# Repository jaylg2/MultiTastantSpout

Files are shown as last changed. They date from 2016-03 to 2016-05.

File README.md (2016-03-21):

# MultiTastantSpout
This directory contains open source design materials for a rodent behavioral environment for learning from positive and negative events. These materials are for an Arduino controlled lick spout that controls delivery of small amounts of three different tastants, playing of 2 different tones (11KHz and 4KHz in this design), and timing of an in-cage light cue. 

See MultiTast_Overview for information on the build

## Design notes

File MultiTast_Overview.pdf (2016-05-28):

MultiTastant Spout
Construction Instructions
Nathan V-C, Ph.D.
3/9/2016

Overview:
This directory contains open source design materials for a rodent behavioral environment for learning from positive and negative events. These materials are for an Arduino controlled lick spout that controls delivery of small amounts of three different tastants, playing of 2 different audio cue tones (11KHz and 4KHz in this design), and timing of an in-cage light cue.

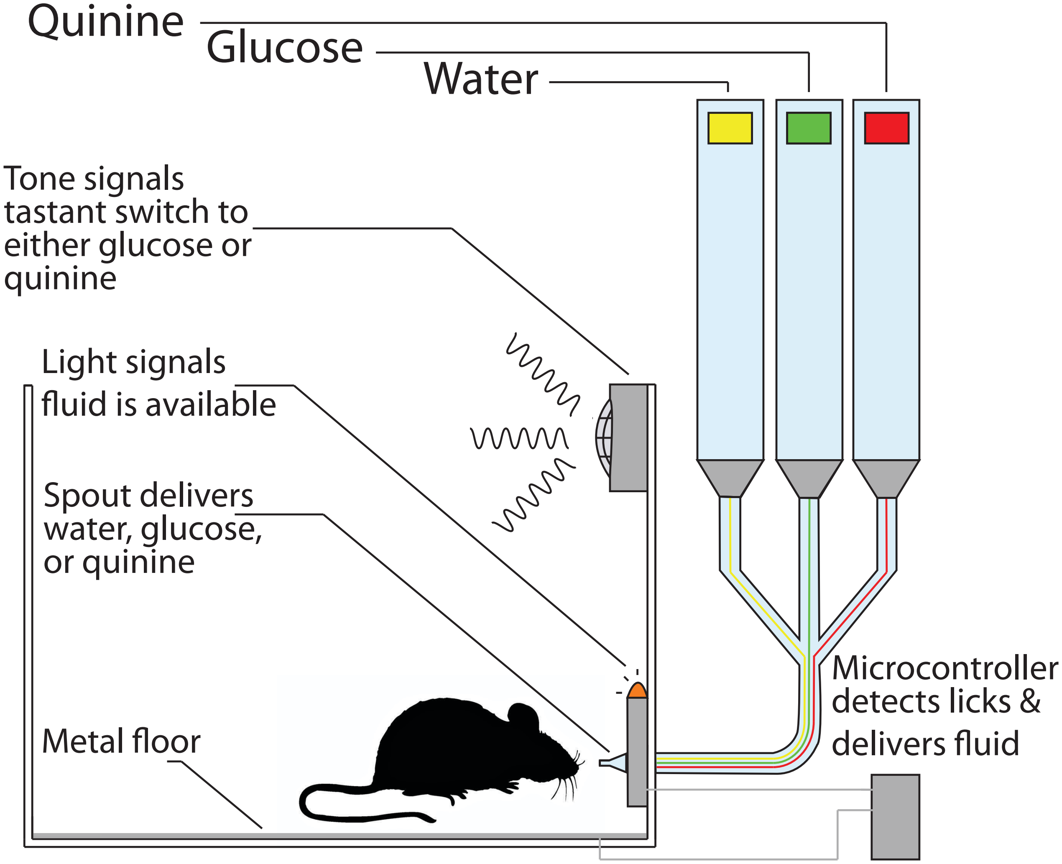
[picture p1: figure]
Quinine Glucose Water; Tone signals tastant switch to either glucose or quinine; Light signals fluid is available; Spout delivers water, glucose, or quinine; Metal floor; Microcontroller detects licks & delivers fluid

Overall the system contains three components:

### 1. Spout Control Board (Arduino Uno Shield)

Eagle and Gerber design files contained in: 3tastsp_v7_resistorcooldrive_battcheck/
This is an Arduino shield contains hardware to control solenoid valves that deliver tastants, LED lights that inform the experimentalist about task events, a calibration button, location for analog-input signal that cues trial type, location for the raw analog input lick signal (through BNC connectors), and an HDMI plug that transmits 8 digital output data signals to your preferred data acquisition system. This control board is placed outside of the behavioral environment (typically a closed sound attenuated cupboard or box). This circuit board design can be sent out to a fabrication company. I use Seeedstudio and these gerber files match their production requirements.

### 2. Spout Interface Board

Eagle and Gerber design files contained in: sptinterface_v4_battcheck/

This printed circuit board delivers cues and power to the solenoid valves that control tastant delivery, the internal cage cue light, some circuitry to protect the lick signal voltage from noise and current draw elsewhere in the system, and produces two cue tones using 555 timer circuits. This board needs to be placed near the spout assembly (typically inside the behavioral enclosure, near but not inside the cage). This design has a feature that if you wish to switch to IR lick detection, there is a plug and circuitry available for that. With this design you must choose between a raw voltage signal lick detection (where the mouse is on a grounded metal cage floor) and IR lick detection. The current spout design does not support IR detection but this is do-able, and this board is set up both to run 5V power to an IR emitter, and to detect analog output from an IR detector. Also, the lick detection circuit is consolidated to the left of the board, with separation possible from the right part of the board that generates tones and controls valves. I designed this board this way so the same system can be adapted to a system where valves need to be separate from the spout (for example, when combined with electrophysiological recording). This PCB can be sent out to a fabrication company. I use Seeedstudio and these gerber files match their production requirements.

### 3. Spout Assembly

OpenSCAD and .stl design files contained in: spoutassembly/
The spout itself is hand built from thin steel 24 gauge tubing arranged in a cylinder and that then interfaces with barbed connectors to link to solenoid valves that deliver the tastant. This spout assembly also holds the solenoid valves. 3 wires from the spout connect to the Spout Interface Board, the LED power, Ground, and a wire connected to the metal spout. I’ve included an OpenSCAD and .stl file of the parts needed for the spout assembly here

These three components are included in these design files. In addition to these three components, you will need a source to generate an analog input signal that cues trial type (I use a NIDAQ card), and Arduino UNO (loaded Arduino script PCB_3tast_v29_3tnblank_public_switchpins.ino or your own modification), a cage and behavioral enclosure, a set of computer speakers to play the tones, and a 9V battery to power the tone production.

At this time, an initial nearly complete parts list is available in this directory (excel file). Construction instructions are still being compiled, but if you would like to build a rig like this and need more complete information before I have updated, please don’t hesitate to contact me via github.

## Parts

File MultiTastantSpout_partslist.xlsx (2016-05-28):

Multitastant spout parts list and cost calculator (Not including data acquisiton or computer) |  |  |  |  |  | Total Cost/rig: | $447.11
Enter number of each component you are ordering parts for: |  | 5 | 5 | 5 |  | Cost/order: | $2235.56
Calculate Cost per single version of each component: |  | $120.74 | $15.28 | $311.09
Type of Part | Link | Control | Spt Interface | Spout | Cost/each | Cost/setup | Cost/Control | Cost/Interface | Cost/Spout
Arduino Uno microcontroller | https://www.sparkfun.com/products/11021 | 1 | 0 | 0 | $24.95 | $24.95 | $24.95 | $0.00 | $0.00
Set of four colored LEDs (one each: red/green/yellow/blue) | https://www.sparkfun.com/products/12062 | 1 | 0 | 0 | $0.59 | $0.59 | $0.59 | $0.00 | $0.00
Tactile button (sparkfun) | https://www.sparkfun.com/products/9190 | 1 | 0 | 0 | $0.50 | $0.50 | $0.50 | $0.00 | $0.00
9-pin female connectors (digikey) | http://www.digikey.com/product-detail/en/PPPC091LFBN-RC/S7042-ND/810181 | 4 | 0 | 0 | $0.69 | $2.76 | $2.76 | $0.00 | $0.00
HDMI connector | http://www.digikey.com/product-search/en?pv7=2&k=609-4614-1-ND&mnonly=0&newproducts=0&ColumnSort=0&page=1&quantity=0&ptm=0&fid=0&pageSize=25 | 1 | 0 | 0 | $0.69 | $0.69 | $0.69 | $0.00 | $0.00
BNC male connectors | http://www.mouser.com/ProductDetail/TE-Connectivity-AMP/1-1337543-0/?qs=sGAEpiMZZMvlX3nhDDO4AKImBYvddvkFKOqsKyyMJX4= | 2 | 2 | 0 | $1.15 | $4.60 | $2.30 | $2.30 | $0.00
Male 4-wall 16 pin ribbon connector port (3M) | http://www.mouser.com/ProductDetail/3M-Electronic-Solutions-Division/30316-6002HB/?qs=sGAEpiMZZMujYETmGQpRztX3nUeKjWBk | 1 | 1 | 0 | $0.77 | $1.54 | $0.77 | $0.77 | $0.00
Shield pins to connect to Arduino (31 pins total needed, order strip of 40): | http://www.digikey.com/product-detail/en/4-103741-0/A26509-40-ND/297917 | 1 | 0 | 0 | $1.82 | $1.82 | $1.82 | $0.00 | $0.00
330 Ohm resistors | http://www.digikey.com/product-detail/en/stackpole-electronics-inc/CF14JT330R/CF14JT330RCT-ND/1830338 | 4 | 2 | 0 | $0.04 | $0.24 | $0.16 | $0.08 | $0.00
10K resistors | http://www.digikey.com/product-detail/en/stackpole-electronics-inc/CF14JT10K0/CF14JT10K0CT-ND/1830374 | 1 | 1 | 0 | $0.04 | $0.08 | $0.04 | $0.04 | $0.00
1K resistors | http://www.digikey.com/product-detail/en/stackpole-electronics-inc/CF14JT1K00/CF14JT1K00CT-ND/1830350 | 4 | 4 | 0 | $0.04 | $0.32 | $0.16 | $0.16 | $0.00
8 Pin DIP sockets | http://www.digikey.com/product-detail/en/DILB8P-223TLF/609-4717-ND/4292069 | 0 | 3 | 0 | $0.17 | $0.52 | $0.00 | $0.52 | $0.00
TIP122 NPN Transistors | http://www.digikey.com/product-detail/en/TIP122/TIP122FS-ND/458797 | 0 | 3 | 0 | $0.54 | $1.62 | $0.00 | $1.62 | $0.00
555 timers | http://www.digikey.com/product-search/en?x=0&y=0&lang=en&site=us&keywords=LM555CNNS | 0 | 2 | 0 | $0.93 | $1.87 | $0.00 | $1.87 | $0.00
9 Volt battery holder | http://www.digikey.com/product-detail/en/BH9VPC/BH9V-PC-ND/31510 | 0 | 1 | 0 | $1.60 | $1.60 | $0.00 | $1.60 | $0.00
3-pin shrouded male connector | http://www.digikey.com/product-detail/en/5-103735-2/A33924-ND/1122487 | 0 | 3 | 0 | $1.05 | $3.15 | $0.00 | $3.15 | $0.00
4-pin shrouded male connector for IR option | http://www.digikey.com/product-detail/en/te-connectivity-amp-connectors/5-103735-3/A33926-ND/1122489 | 0 | 1 | 0 | $1.66 | $1.66 | $0.00 | $1.66 | $0.00
Crimp connectors | http://www.digikey.com/product-detail/en/1-104479-3/A34249-ND/11258912 | 0 | 0 | 12 | $0.23 | $2.71 | $0.00 | $0.00 | $2.71
1-pin shrouded connector socket | http://www.digikey.com/product-detail/en/te-connectivity-amp-connectors/1-1123824-1/A30708-ND/686939 | 0 | 0 | 2 | $0.19 | $0.38 | $0.00 | $0.00 | $0.38
1-pin plug for shielding | http://www.digikey.com/product-detail/en/te-connectivity-amp-connectors/1-1123823-1/A30525-ND/686690 | 0 | 0 | 1 | $0.10 | $0.10 | $0.00 | $0.00 | $0.10
1-pin connector crimp connections | http://www.digikey.com/product-detail/en/te-connectivity-amp-connectors/1123721-2/A100446CT-ND/2233212 | 0 | 0 | 1 | $0.17 | $0.17 | $0.00 | $0.00 | $0.17
2-pin shrouded male connectors for valves | http://www.digikey.com/product-detail/en/5-103735-1/A33921-ND/1122484 | 0 | 0 | 4 | $0.70 | $2.80 | $0.00 | $0.00 | $2.80
LM258N op-amp | http://www.digikey.com/product-detail/en/LM258N/LM258NFS-ND/1051227 | 0 | 0 | 1 | $0.45 | $0.45 | $0.00 | $0.00 | $0.45
Female 16 pin ribbon connector socket for ribbon cable (3M) | http://www.mouser.com/ProductDetail/3M-Electronic-Solutions-Division/89116-0101/ | 0 | 0 | 2 | $1.05 | $2.10 | $0.00 | $0.00 | $2.10
1.5 Kohms resistor (brown, green, red, gold bands, for ~4KHz tone) | http://www.digikey.com/product-detail/en/stackpole-electronics-inc/CF14JT1K50/CF14JT1K50CT-ND/1830354 | 0 | 1 | 0 | $0.04 | $0.04 | $0.00 | $0.04 | $0.00
270 Kohm resistor (red, purple, yellow, gold, for ~4KHz tone | http://www.digikey.com/product-detail/en/stackpole-electronics-inc/CF14JT270K/CF14JT270KCT-ND/1830409 | 0 | 1 | 0 | $0.04 | $0.04 | $0.00 | $0.04 | $0.00
680 Ohm resistor (blue, gray, brown, gold, for ~11KHz tone) | http://www.digikey.com/product-detail/en/stackpole-electronics-inc/CF14JT680R/CF14JT680RCT-ND/1830346 | 0 | 1 | 0 | $0.04 | $0.04 | $0.00 | $0.04 | $0.00
100 KOhms (brown, black, yellow, gold, for ~11KHz tone) | http://www.digikey.com/product-detail/en/stackpole-electronics-inc/CF14JT100K/CF14JT100KCT-ND/1830399 | 0 | 1 | 0 | $0.04 | $0.04 | $0.00 | $0.04 | $0.00
capacitors for 555 timers (need to check value) | http://www.digikey.com/product-detail/en/FK28C0G1H561J/445-4735-ND/2050084 | 0 | 2 | 0 | $0.23 | $0.47 | $0.00 | $0.47 | $0.00
Voltage regulators | http://www.digikey.com/product-detail/en/LM7805CT/LM7805CT-ND/458698 | 0 | 1 | 0 | $0.62 | $0.62 | $0.00 | $0.62 | $0.00
1A diodes for tone circuit | http://www.digikey.com/product-detail/en/micro-commercial-co/1N4002-TP/1N4002-TPMSCT-ND/773689 | 0 | 2 | 0 | $0.11 | $0.22 | $0.00 | $0.22 | $0.00
3A diodes for valves | http://www.digikey.com/product-detail/en/fairchild-semiconductor/1N5401/1N5401FSCT-ND/1532774 | 0 | 0 | 4 | $0.31 | $1.24 | $0.00 | $0.00 | $1.24
27 KOhm resistor to reduce volume of lower tone (red, purple, orange, gold) | http://www.digikey.com/product-detail/en/stackpole-electronics-inc/CF14JT27K0/CF14JT27K0CT-ND/1830385 | 0 | 1 | 0 | $0.04 | $0.04 | $0.00 | $0.04 | $0.00
2 ¼” bright white LEDs (sparkfun link) | https://www.sparkfun.com/products/9850 | 0 | 0 | 2 | $0.32 | $0.64 | $0.00 | $0.00 | $0.64
1 shrouded 4-pin female connector | http://www.digikey.com/product-detail/en/te-connectivity-amp-connectors/104257-3/A28401-ND/289304 | 0 | 0 | 1 | $0.56 | $0.56 | $0.00 | $0.00 | $0.56
1 shrouded 3 pin female connector | http://www.digikey.com/product-detail/en/104257-2/A28397-ND/289303 | 0 | 0 | 1 | $0.49 | $0.49 | $0.00 | $0.00 | $0.49
BNC T connector (for splitting lick signal to data collection if desired) | http://www.digikey.com/product-detail/en/27-8141/J10096-ND/698063 | 1 | 0 | 0 | $3.00 | $3.00 | $3.00 | $0.00 | $0.00
HDMI cable (for connecting control board to data collection) | http://www.amazon.com/gp/product/B0052SCU8U/ref=ox_sc_act_title_3?ie=UTF8&psc=1&smid=ATVPDKIKX0DER | 1 | 0 | 0 | $3.00 | $3.00 | $3.00 | $0.00 | $0.00
Power cord for Arduino (12V, 1A, less than 1A is not enough power for valves) |  |  |  |  |  | $0.00 | $0.00 | $0.00 | $0.00
Computer speakers | http://www.amazon.com/gp/product/B000R9AAJA/ref=ox_sc_act_title_1?ie=UTF8&psc=1&smid=ATVPDKIKX0DER | 0 | 0 | 1 | $16.49 | $16.49 | $0.00 | $0.00 | $16.49
Four two-pin shrouded female connectors for valves | http://www.digikey.com/product-detail/en/te-connectivity-amp-connectors/104257-1/A28393-ND/289301 | 0 | 0 | 4 | $0.39 | $1.56 | $0.00 | $0.00 | $1.56
Female screwmount BNC connector for speakers | ?? |  |  |  |  | $0.00 | $0.00 | $0.00 | $0.00
NR research “normally closed” solenoid valves, part number | http://nrresearch.com | 0 | 0 | 4 | $62.00 | $248.00 | $0.00 | $0.00 | $248.00
Single valve driver, "Cooldrive ONE Single Valve Driver", model 161D1X250 | http://nrresearch.com | 4 | 0 | 0 | $20.00 | $80.00 | $80.00 | $0.00 | $0.00
2-way luer lock valves | ?? | 0 | 0 | 4 |  | $0.00 | $0.00 | $0.00 | $0.00
3-way luer lock valves | http://bit.ly/1YUbjqb | 0 | 0 | 4 | $8.35 | $33.41 | $0.00 | $0.00 | $33.41
24 gauge steel tubing, approx 30" |  |  |  |  |  | $0.00 | $0.00 | $0.00 | $0.00
1/8” tubing (lots, mcmaster) -- price per foot | http://www.mcmaster.com/#5103k32/=ymy2fa | 0 | 0 | 10 |  | $0.00 | $0.00 | $0.00 | $0.00
1/8” barb connectors (WPI) - I used from this kit, but should be possible to order separately | https://www.wpiinc.com/products/laboratory-supplies/500890-barb-to-tubing-coupler-kit/ | 0 | 0 | 4 |  | $0.00 | $0.00 | $0.00 | $0.00
screw-in Luer Lock connectors for valves (McMaster) | http://www.mcmaster.com/#51525k21/=ymxy71 | 0 | 0 | 8 |  | $0.00 | $0.00 | $0.00 | $0.00
luer lock connection for tubing | http://www.mcmaster.com/#51525k33/=ymxj06 | 0 | 0 | 8 |  |  |  |  | $0.00
Ribbon cable (?? Not sure where to get this, 16 contacts, flat, gray, fits 3M connectors) | ?? |  |  |  |  | $0.00 | $0.00 | $0.00 | $0.00
Other Supplies:
Various BNC cables, 2 long, 1 short, depends on needs of your set-up
18-20 gauge wire in colors as desired for color coding
Foil for shielding speaker wire
Heat shrink tubing
Cage, need to be able to open hole in side for spout, and attach metal tape to floor
10 mL syringes to serve as fluid reservoirs
metal tape for cage floor -- metal tape for duct installation (different than duct tape!) works well
3D printed spout assembly
3D printed syringe reservoir grid and syringe holders
3D printed caps for syringes to keep fluids & valves clean
alligator clip connectors

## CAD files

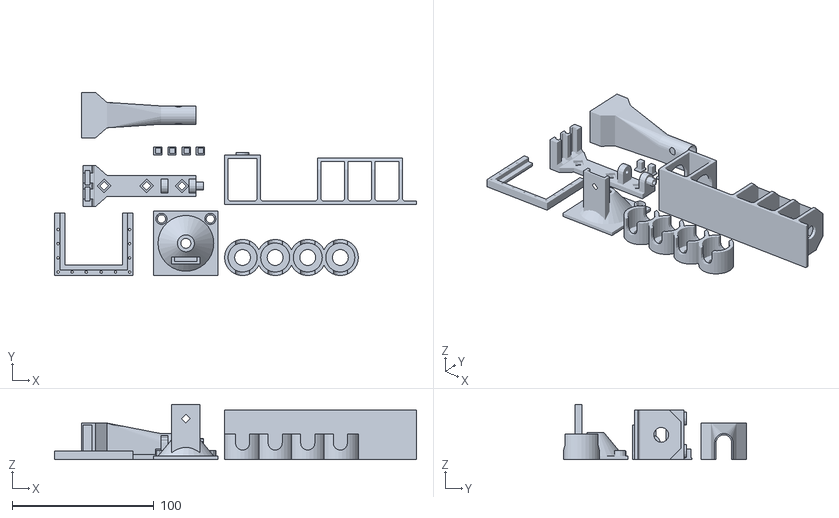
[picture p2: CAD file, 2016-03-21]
spoutassembly/valveandspout_modular_v8_share_allparts.stl
255.5 x 129.2 x 39.0

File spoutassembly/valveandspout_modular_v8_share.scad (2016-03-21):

//------------------
// Generate STL file for multi-tastant spout
//------------------
// Nathan V-C
// 6/2015-10/2015
//------------------

// total height of support from floor of cage
supp_ht=33; 
// total width of support side to side
supp_w=35;
// width at top of support
supp_w_top=10;  // top is actually wider
// length of the spout support portion of the support
supp_ln=60;  
// distance base should extend forward of front edge of spout support
bs_ext=10;

// clearance value -- difference in size for pieces that need to fit in/around each other
cl=1;

// valve dimensions
r_mn=10.25; // radius of solenoid valves
r_big=13; // radius for the large pinch valve
r_tb=5;  // radius of holes for tubes in the valve holder
d_vb=9.2;  // distance to center of tube from flat edge of valve
d_vh=18; // depth of valve holder
th_v=1.5; // thickness for valve holder (for the version with the fluid tray) -- thinner than some other portions (in v6 was the same)

//distance bottom of valves should be from floor of cage -- actually end up thickness higher
v_ht=35; // higher to avoid some tubes running "down" and some running "up" 

thickness=2.5;  // wall thickness throughout assembly
dist_bt=40; // distance between valve support and spout support

// measurements for spout tubing brace attachment
barb_w=10; // width of barb connector
barb_ht=8.4; // height of barb connector
barb_th=3.5; // thickness of barb connector
barb_dpth=1.5;  // depth of groove to hold barb attachments in place
sp_diam=3; // diameter of hole to leave for spout itself (overestimate)

// measurements for nose cone
cn_diam_i=38.5; // inner dimension of nose cone (wall builds around this)
cn_diam_r=6; // inner diameter for opening at back of cone;
cn_depth=19; // depth of cone
led_diam=6; // diameter of hole to leave for LED lights
led_dpth=6.5; // depth of cylinder that LED fits into
led_wall=1;	  // width of wall that holds LED	
led_dist=5.5; // distance of LED hole from edge (dist to center)
br_sq=45.5; // dimension for square part of nose cone
center_ht=45;   // height of center of nose cone from floor, greater than supp_ht
l_cn_br=20; // length of cone brace, distance that flange extends beyond rear of cone to hook onto the tubing brace

// calculations for removing material from spout base
h_sz=(supp_ln-4*thickness)/3;
supp_diag=-0.5*sqrt(2*pow(thickness/2,2));
cube_side=2*min(v_ht,supp_w)/5;
cube_diag=0.5*sqrt(2*pow(cube_side,2));
min_dim=min(v_ht,supp_w);

// dimensions for PCB & battery tray
th_sp=2.5; // thickness of walls in the spout attaching to
th=1.5; // thickness of walls in the pcb tray
pcb_l=90.5; // length of pcb tray
pcb_w=40.5; // width of pcb tray
batt_l=55.5; // dimension for 9V holder
batt_w=31;    // dimensions for 9V holder
batt_th=17;
d_flr=5; // distance of bracket from floor
d_spt=5; // distance of pcb from spout base
gv_dpth=2.5;
batt_o=22.5;
batt_e=8; // amount that holder lip overlaps battery
co=25; // how wide to make cutout for ground wires

//**********
//**********
//------------
// modular part generation -- comment in/out to generate parts that you need
//------------

spout_base(0,0,0);
valve_stand_orig(0,-50,0);
tubing_brace(-(supp_ln+l_cn_br+20),0,0);
spout_shield(-(supp_ln+l_cn_br+20),50,0,1,.5);
nose_cone(-50,-50,0);
cage_bracket(-120,-50,0);

lock_hole_pin(-20,35,0);
lock_hole_pin(-30,35,0);
lock_hole_pin(-40,35,0);
lock_hole_pin(-50,35,0);

// items specific to nathan's set-up
// pcb_tray(0,v_ht+30,0);
// valve_stand_fluidcont(0,-50,0);

//***********
//***********

//---------------------
// Spout base
//----------------------

module spout_base(xp,yp,zp){

translate([xp,yp,zp])

	union(){
		union(){
			difference(){
				union(){
					// spout support
					translate([dist_bt+2*thickness+2*r_mn,0,0])cube([supp_ln,supp_ht,supp_w]);
					//base
					cube([supp_ln+bs_ext+dist_bt+2*thickness+2*r_mn,thickness,supp_w]);
					//valve support
					cube([r_mn*2+2*thickness,v_ht,supp_w]);
					// small circles to help hold valve holder onto support
					translate([thickness+r_mn,v_ht+0.75*thickness,supp_w/2-r_mn-thickness/2])rotate(90,[1,0,0])cylinder(h=thickness, r=r_mn/2-.5,center=false);
					translate([thickness+r_mn,v_ht+0.75*thickness,supp_w/2+r_mn+thickness/2])rotate(90,[1,0,0])cylinder(h=thickness, r=r_mn/2-.5,center=false);
					//extra support for seams
					translate([2*r_mn+2*thickness,supp_diag+thickness/2,0])rotate(45,[0,0,1])cube([thickness,thickness,supp_w]);	
					translate([2*r_mn+2*thickness+dist_bt,supp_diag+thickness/2,0])rotate(45,[0,0,1])cube([thickness,thickness,supp_w]);	
					translate([2*r_mn+2*thickness+dist_bt+supp_ln,supp_diag+thickness/2,0])rotate(45,[0,0,1])cube([thickness,thickness,supp_w]);	
				}
				union(){
					// slant at top of spout support
					translate([-thickness,supp_ht,-0.5*sqrt(2*pow((supp_ht-supp_w_top)/2,2))])rotate(45,[1,0,0])
					translate([dist_bt+2*thickness+2*r_mn,0,0])cube([supp_ln+2*thickness,(supp_ht-supp_w_top)/2,(supp_ht-supp_w_top)/2]);
			
					translate([-thickness,supp_ht,-0.5*sqrt(2*pow((supp_ht-supp_w_top)/2,2))+supp_w])rotate(45,[1,0,0])
					translate([dist_bt+2*thickness+2*r_mn,0,0])cube([supp_ln+2*thickness,(supp_ht-supp_w_top)/2,(supp_ht-supp_w_top)/2]);
			
					// remove squares from spout support to reduce volume
					translate([supp_ln-thickness-h_sz+dist_bt+2*thickness+2*r_mn,thickness,-thickness])cube([h_sz,supp_ht-2*thickness,supp_w+2*thickness]);
					translate([supp_ln-2*thickness-2*h_sz+dist_bt+2*thickness+2*r_mn,thickness,-thickness])cube([h_sz,supp_ht-2*thickness,supp_w+2*thickness]);
					translate([supp_ln-3*thickness-3*h_sz+dist_bt+2*thickness+2*r_mn,thickness,-thickness])cube([h_sz,supp_ht-2*thickness,supp_w+2*thickness]);
			
					// remove square from valve support
					translate([thickness,thickness,-thickness])cube([2*r_mn,v_ht-2*thickness,supp_w+2*thickness]);
			
					// remove material from valve support base in the x direction, use circles to keep printability in z direction
					translate([-thickness,v_ht/2,supp_w/2])rotate(90,[0,1,0])cylinder(h=4*thickness+2*r_mn, r=min_dim/2-2*thickness);
			
					// remove material from spout support base in the x direction, use circle to keep printability in z direction
					translate([dist_bt+thickness+2*r_mn,supp_ht/2+2.5,supp_w/2])rotate(90,[0,1,0])cylinder(h=2*thickness+supp_ln, r=(supp_ht-supp_w_top-thickness)/2-2*thickness);
			
					// remove locking holes
					union(){
						translate([0.25*supp_ln+dist_bt+2*thickness+2*r_mn,supp_ht-thickness,supp_w/2])rotate(-90,[1,0,0])lock_hole_btm(0,0,0);
						translate([0.75*supp_ln+dist_bt+2*thickness+2*r_mn,supp_ht-thickness,supp_w/2])rotate(-90,[1,0,0])lock_hole_btm(0,0,0);
					}
				}
			}
		}

		// add  back some more extra support for seams
		union(){
			//extra support for seams	
			translate([2*r_mn+2*thickness+dist_bt+thickness,supp_diag+thickness/2,0])rotate(45,[0,0,1])cube([thickness,thickness,supp_w]);	
			translate([2*r_mn+2*thickness+dist_bt+thickness+h_sz,supp_diag+thickness/2,0])rotate(45,[0,0,1])cube([thickness,thickness,supp_w]);	
			translate([2*r_mn+2*thickness+dist_bt+2*thickness+h_sz,supp_diag+thickness/2,0])rotate(45,[0,0,1])cube([thickness,thickness,supp_w]);	
			translate([2*r_mn+2*thickness+dist_bt+2*thickness+2*h_sz,supp_diag+thickness/2,0])rotate(45,[0,0,1])cube([thickness,thickness,supp_w]);	
			translate([2*r_mn+2*thickness+dist_bt+3*thickness+2*h_sz,supp_diag+thickness/2,0])rotate(45,[0,0,1])cube([thickness,thickness,supp_w]);	
			translate([2*r_mn+2*thickness+dist_bt+3*thickness+3*h_sz,supp_diag+thickness/2,0])rotate(45,[0,0,1])cube([thickness,thickness,supp_w]);	
			translate([thickness,supp_diag+thickness/2,0])rotate(45,[0,0,1])cube([thickness,thickness,supp_w]);	
			translate([thickness+2*r_mn,supp_diag+thickness/2,0])rotate(45,[0,0,1])cube([thickness,thickness,supp_w]);	
		}
	}
}

//-----------------------
// separate stand for valves, include one slot for large pinch valve
//----------------------

module valve_stand_large(xp,yp,zp){

translate([xp,yp,zp])
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

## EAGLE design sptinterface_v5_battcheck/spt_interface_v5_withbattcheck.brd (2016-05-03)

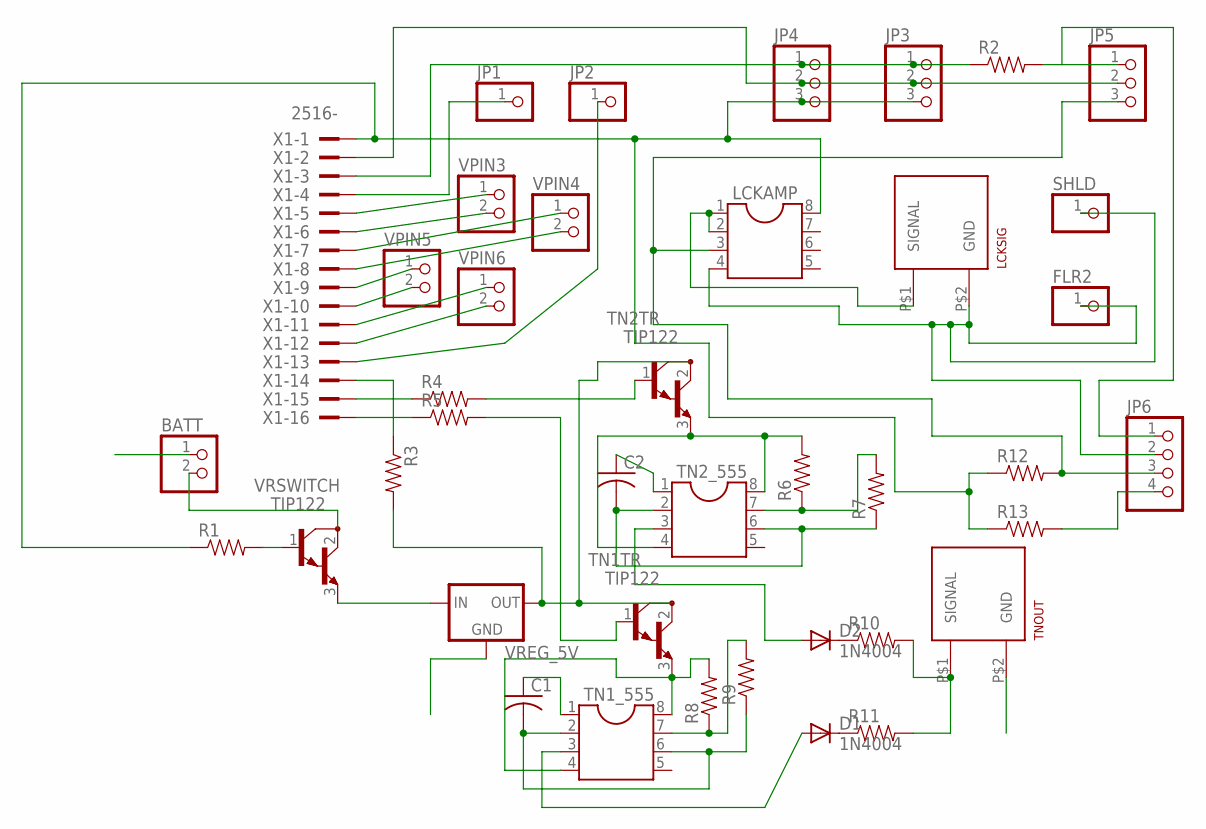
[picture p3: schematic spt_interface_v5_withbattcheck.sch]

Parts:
BATT: PINHD-1X2; 1X02
C1, C2: C-US050-024X044; C050-024X044
D1, D2: 1N4004; DO41-10
FLR2: PINHD-1X1; 1X01
JP1, JP2: PINHD-1X1; 1X01
JP3, JP4, JP5: PINHD-1X3; 1X03
JP6: PINHD-1X4; 1X04
LCKAMP: DIL8; DIL08
LCKSIG: BNC_VERTICAL
R1, R2, R3, R4, R5, R6, R7, R8, R9, R10, R11, R12, R13: 1KOHM-1/4W-5%(PTH)HORIZ-KIT; AXIAL-0.3EZ
SHLD: PINHD-1X1; 1X01
TN1TR, TN2TR: TIP122; TO220
TN1_555, TN2_555: DIL8; DIL08
TNOUT: BNC_VERTICAL
VPIN3, VPIN4, VPIN5, VPIN6: PINHD-1X2; 1X02
VREG_5V: 78XXL
VRSWITCH: TIP122; TO220
X1: 2516-; PAK100/2500-16

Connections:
GND: BATT.1, C1.1, C2.1, FLR2.1, JP3.2, JP4.2, JP5.2, JP6.2, LCKAMP.4, LCKSIG.P$2 (GND), SHLD.1, TN1_555.1, TN2_555.1, TNOUT.P$2 (GND), VREG_5V.GND, X1.2
unnamed: R3.P$1 (1), X1.14
unnamed: BATT.2, VRSWITCH.2 (C)
unnamed: R4.P$2 (2), TN2TR.1 (B)
unnamed: R5.P$2 (2), TN1TR.1 (B)
unnamed: R8.P$2 (2), TN1TR.3 (E), TN1_555.4, TN1_555.8
unnamed: D2.C, R10.P$1 (1)
unnamed: R4.P$1 (1), X1.15
unnamed: JP3.3, JP4.3, LCKAMP.8, R1.P$1 (1), R12.P$1 (1), R13.P$1 (1), X1.1
unnamed: D1.A, TN1_555.3
unnamed: LCKAMP.1, LCKAMP.2, LCKSIG.P$1 (SIGNAL)
unnamed: R6.P$1 (1), R7.P$2 (2), TN2_555.7
unnamed: R8.P$1 (1), R9.P$2 (2), TN1_555.7
unnamed: C2.2, R7.P$1 (1), TN2_555.2, TN2_555.6
unnamed: C1.2, R9.P$1 (1), TN1_555.2, TN1_555.6
unnamed: D2.A, TN2_555.3
unnamed: VPIN5.1, X1.9
unnamed: R10.P$2 (2), R11.P$2 (2), TNOUT.P$1 (SIGNAL)
unnamed: JP3.1, JP4.1, R2.P$1 (1), X1.3
unnamed: JP5.1, JP6.1, R2.P$2 (2)
unnamed: VPIN3.1, X1.5
unnamed: VPIN3.2, X1.6
unnamed: VPIN4.1, X1.7
unnamed: VPIN4.2, X1.8
unnamed: VPIN5.2, X1.10
unnamed: VPIN6.1, X1.11
unnamed: VPIN6.2, X1.12
unnamed: R6.P$2 (2), TN2TR.3 (E), TN2_555.4, TN2_555.8
unnamed: JP5.3, JP6.3, LCKAMP.3, R12.P$2 (2)
unnamed: VREG_5V.IN, VRSWITCH.3 (E)
unnamed: JP1.1, X1.4
unnamed: JP2.1, X1.13
unnamed: R1.P$2 (2), VRSWITCH.1 (B)
unnamed: D1.C, R11.P$1 (1)
unnamed: R5.P$1 (1), X1.16
unnamed: R3.P$2 (2), TN1TR.2 (C), TN2TR.2 (C), VREG_5V.OUT
unnamed: JP6.4, R13.P$2 (2)

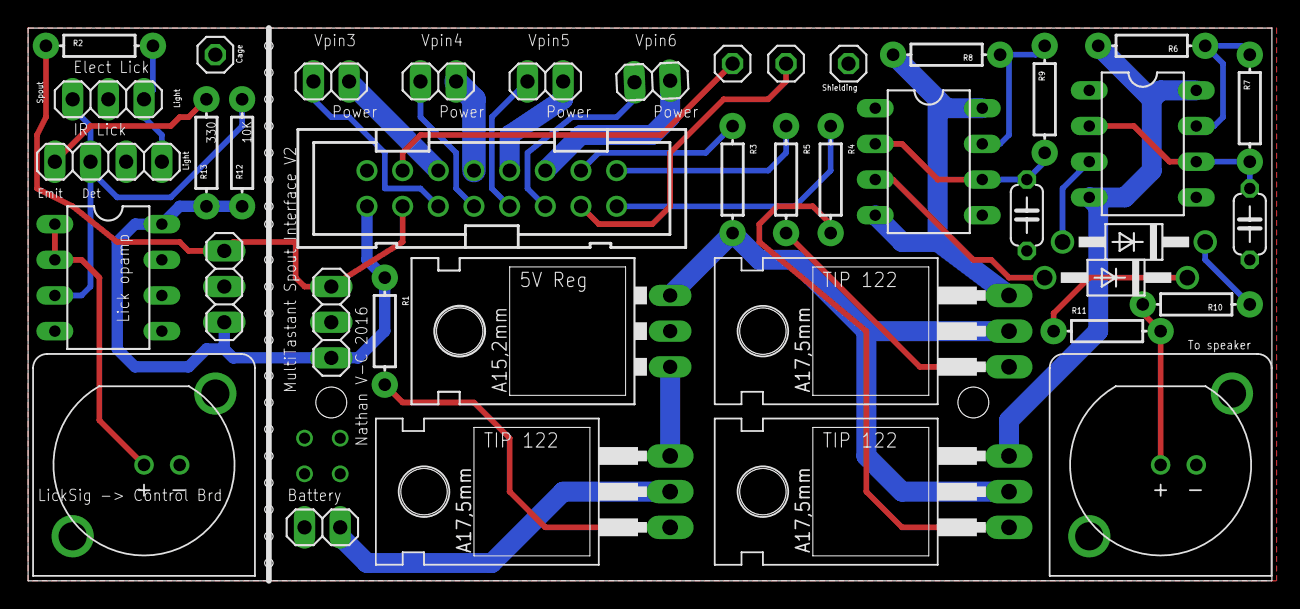
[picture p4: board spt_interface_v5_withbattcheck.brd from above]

Board: 2 copper layers, 88.6 x 39.4 mm, 40 parts (0 on the bottom side), 37 nets.

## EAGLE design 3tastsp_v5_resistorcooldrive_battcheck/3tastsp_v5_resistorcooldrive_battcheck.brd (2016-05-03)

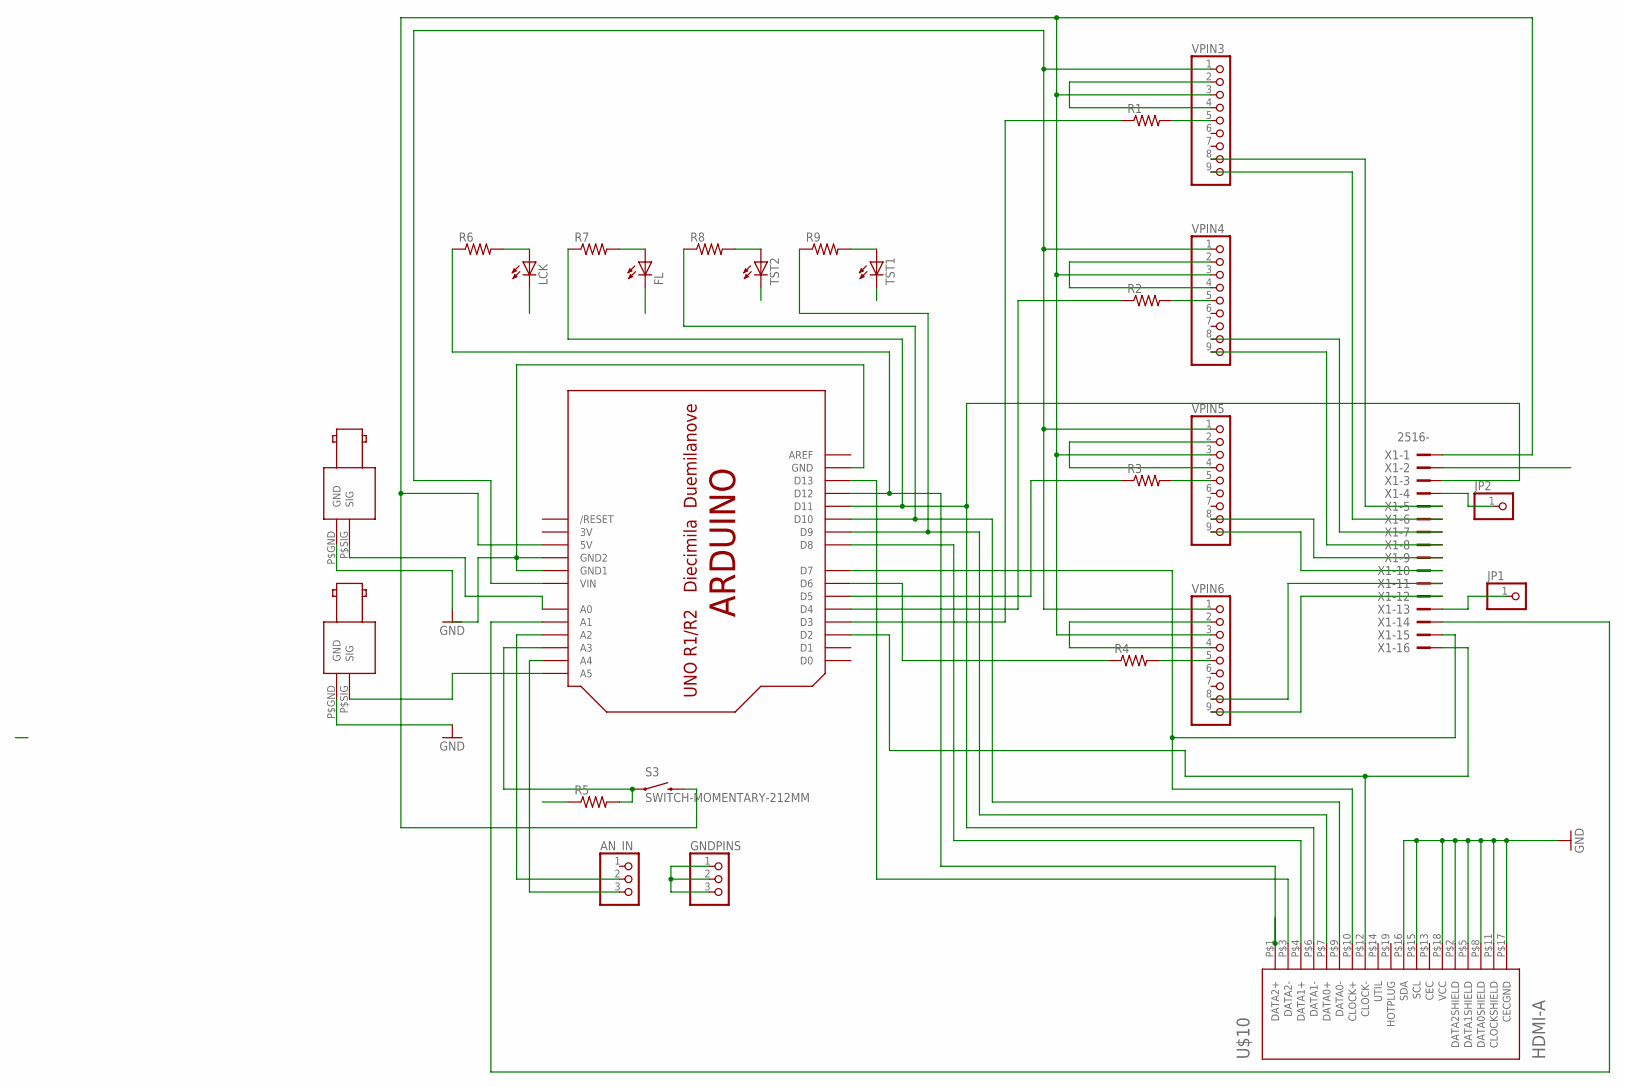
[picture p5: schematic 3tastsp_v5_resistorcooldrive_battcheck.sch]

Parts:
AN_IN: PINHD-1X3; 1X03
FL: LED5MM
GNDPINS: PINHD-1X3; 1X03
JP1, JP2: PINHD-1X1; 1X01
LCK: LED5MM
LICKSIG: BNC_RIGHT_ANGLE
R1, R2, R3, R4, R5, R6, R7, R8, R9: 1KOHM-1/4W-1%(PTH)HORIZ-KIT; AXIAL-0.3EZ
S3: SWITCH-MOMENTARY-212MM; TACTILE-PTH-12MM
TRIALSIG: BNC_RIGHT_ANGLE
TST1, TST2: LED5MM
U$1: ARDUINO-NOHOLE
U$10: HDMI-A; HDMI_A
VPIN3, VPIN4, VPIN5, VPIN6: PINHD-1X9; 1X09
X1: 2516-; PAK100/2500-16

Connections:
3V: U$1.3V
D6: U$1.D13, U$10.P$3 (DATA2-)
D7: R6.P$1 (1), U$1.D12, U$10.P$1 (DATA2+)
D8: U$1.D8, U$10.P$4 (DATA1+)
D9: R7.P$1 (1), U$1.D11, U$10.P$6 (DATA1-), X1.3
D10: R9.P$1 (1), U$1.D9, U$10.P$7 (DATA0+)
D11: R8.P$1 (1), U$1.D10, U$10.P$9 (DATA0-)
D12: U$1.D7, U$10.P$10 (CLOCK+), X1.15
D13: U$1.D2, U$10.P$12 (CLOCK-), X1.16
GND: FL.K (C), GNDPINS.1, GNDPINS.2, GNDPINS.3, LCK.K (C), LICKSIG.P$GND (GND), R5.P$1 (1), TRIALSIG.P$GND (GND), TST1.K (C), TST2.K (C), U$1.GND, U$1.GND1, U$1.GND2, U$10.P$2 (DATA2SHIELD), U$10.P$5 (DATA1SHIELD), U$10.P$8 (DATA0SHIELD), U$10.P$11 (CLOCKSHIELD), U$10.P$15 (SCL), U$10.P$16 (SDA), U$10.P$17 (CECGND), U$10.P$18 (VCC), VPIN3.2, VPIN3.4, VPIN4.2, VPIN4.4, VPIN5.2, VPIN5.4, VPIN6.2, VPIN6.4, X1.2
unnamed: S3.3 (2), U$1.5V, VPIN3.3, VPIN4.3, VPIN5.3, VPIN6.3, X1.1
unnamed: TRIALSIG.P$SIG (SIG), U$1.A5
unnamed: LICKSIG.P$SIG (SIG), U$1.A0
unnamed: LCK.A, R6.P$2 (2)
unnamed: FL.A, R7.P$2 (2)
unnamed: R8.P$2 (2), TST2.A
unnamed: R9.P$2 (2), TST1.A
unnamed: R1.P$2 (2), VPIN3.5
unnamed: AN_IN.3, U$1.A4
unnamed: AN_IN.2, U$1.A2
unnamed: R2.P$2 (2), VPIN4.5
unnamed: R4.P$1 (1), U$1.D6
unnamed: R3.P$1 (1), U$1.D5
unnamed: R2.P$1 (1), U$1.D4
unnamed: R1.P$1 (1), U$1.D3
unnamed: JP2.1, X1.4
unnamed: R5.P$2 (2), S3.1, U$1.A3
unnamed: U$1.VIN, VPIN3.1, VPIN4.1, VPIN5.1, VPIN6.1
unnamed: VPIN3.8, X1.5
unnamed: VPIN3.9, X1.6
unnamed: VPIN4.8, X1.7
unnamed: VPIN4.9, X1.8
unnamed: VPIN5.9, X1.10
unnamed: VPIN5.8, X1.9
unnamed: VPIN6.8, X1.11
unnamed: VPIN6.9, X1.12
unnamed: R3.P$2 (2), VPIN5.5
unnamed: R4.P$2 (2), VPIN6.5
unnamed: U$1.A1, X1.14
unnamed: JP1.1, X1.13

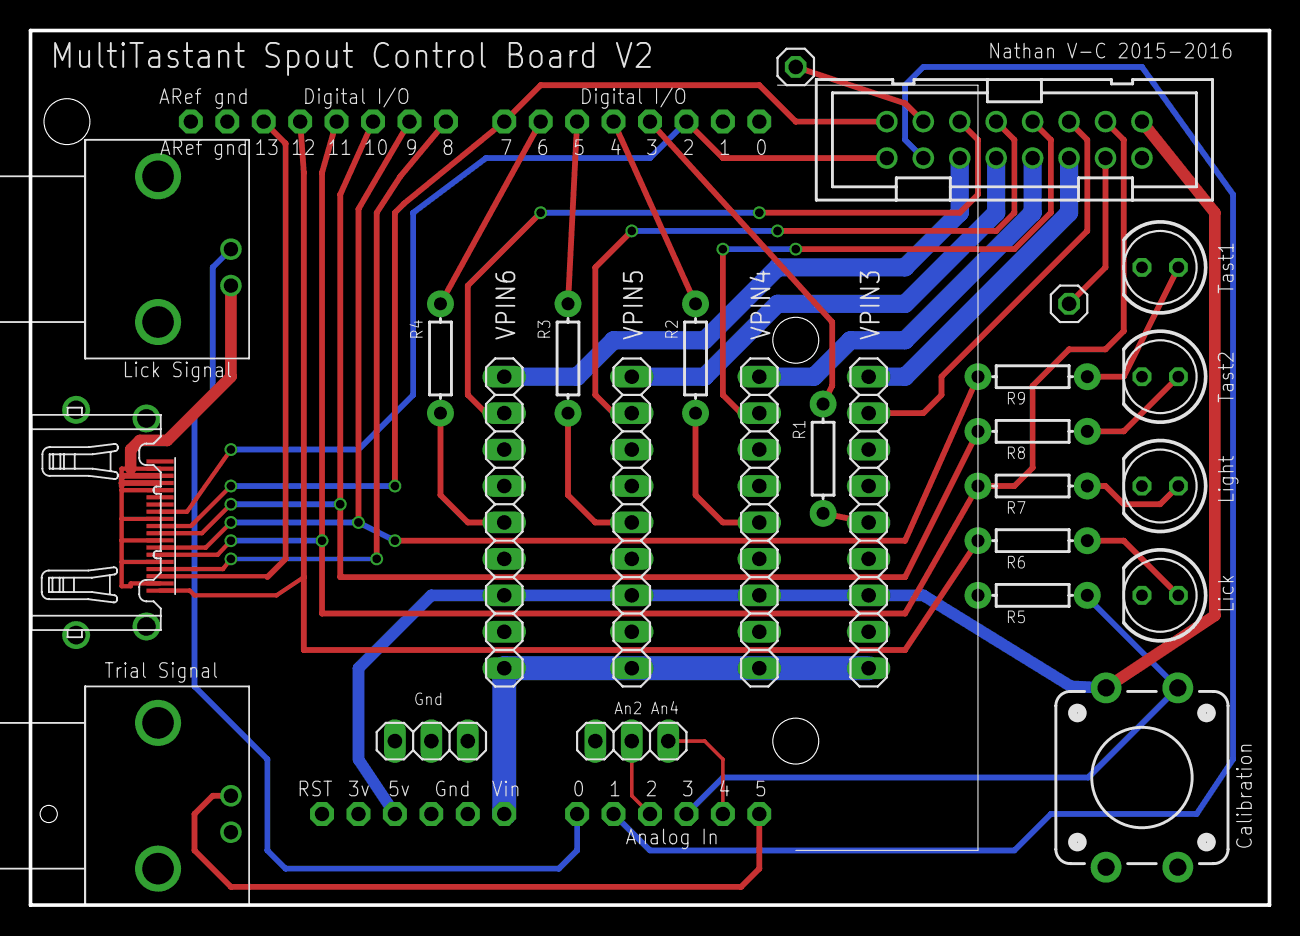
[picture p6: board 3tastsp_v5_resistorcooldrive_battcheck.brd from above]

Board: 2 copper layers, 86.4 x 61.0 mm, 27 parts (0 on the bottom side), 39 nets.

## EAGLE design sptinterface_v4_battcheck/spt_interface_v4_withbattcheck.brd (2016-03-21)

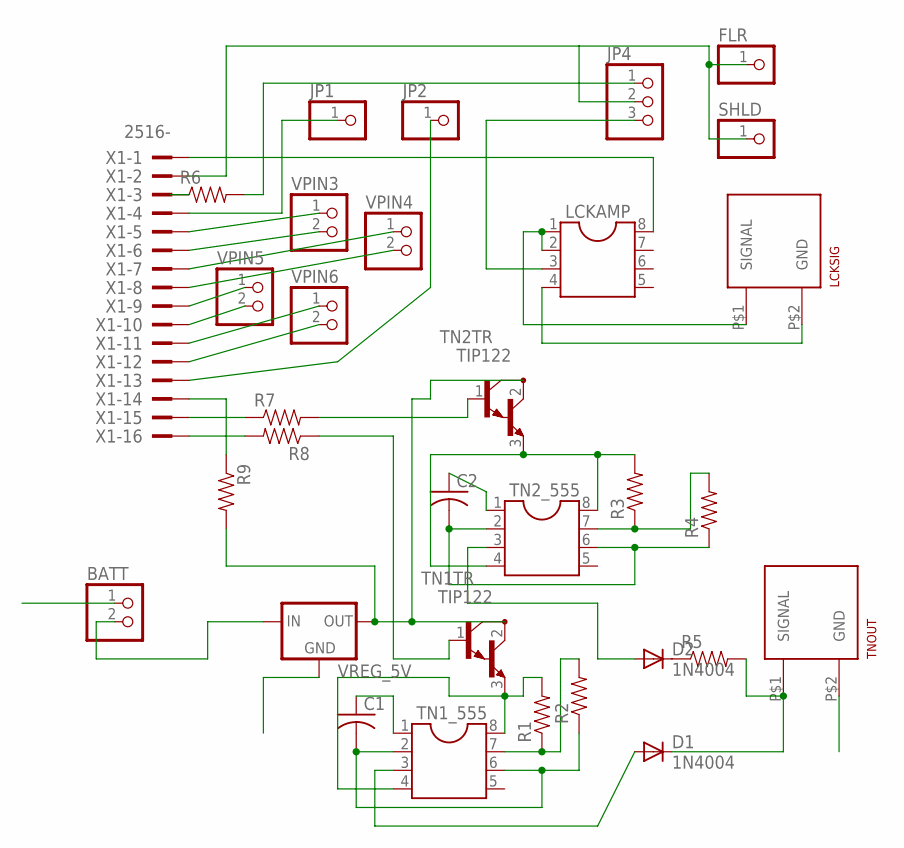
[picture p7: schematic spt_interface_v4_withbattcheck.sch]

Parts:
BATT: PINHD-1X2; 1X02
C1, C2: C-US050-024X044; C050-024X044
D1, D2: 1N4004; DO41-10
FLR: PINHD-1X1; 1X01
JP1, JP2: PINHD-1X1; 1X01
JP4: PINHD-1X3; 1X03
LCKAMP: DIL8; DIL08
LCKSIG: BNC_VERTICAL
R1, R2, R3, R4, R5, R6, R7, R8, R9: RESISTORPTH-1/2W; AXIAL-0.5
SHLD: PINHD-1X1; 1X01
TN1TR, TN2TR: TIP122; TO220
TN1_555, TN2_555: DIL8; DIL08
TNOUT: BNC_VERTICAL
VPIN3, VPIN4, VPIN5, VPIN6: PINHD-1X2; 1X02
VREG_5V: 78XXL
X1: 2516-; PAK100/2500-16

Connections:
GND: BATT.1, C1.1, C2.1, FLR.1, JP4.2, LCKAMP.4, LCKSIG.P$2 (GND), SHLD.1, TN1_555.1, TN2_555.1, TNOUT.P$2 (GND), VREG_5V.GND, X1.2
unnamed: R9.P$1 (1), X1.14
unnamed: BATT.2, VREG_5V.IN
unnamed: R7.P$2 (2), TN2TR.1 (B)
unnamed: R8.P$1 (1), TN1TR.1 (B)
unnamed: R1.P$2 (2), TN1TR.3 (E), TN1_555.4, TN1_555.8
unnamed: D2.C, R5.P$1 (1)
unnamed: R7.P$1 (1), X1.15
unnamed: LCKAMP.8, X1.1
unnamed: D1.A, TN1_555.3
unnamed: LCKAMP.1, LCKAMP.2, LCKSIG.P$1 (SIGNAL)
unnamed: R3.P$1 (1), R4.P$2 (2), TN2_555.7
unnamed: R1.P$1 (1), R2.P$2 (2), TN1_555.7
unnamed: C2.2, R4.P$1 (1), TN2_555.2, TN2_555.6
unnamed: C1.2, R2.P$1 (1), TN1_555.2, TN1_555.6
unnamed: D2.A, TN2_555.3
unnamed: VPIN5.1, X1.9
unnamed: D1.C, R5.P$2 (2), TNOUT.P$1 (SIGNAL)
unnamed: JP4.1, R6.P$2 (2)
unnamed: R6.P$1 (1), X1.3
unnamed: VPIN3.1, X1.5
unnamed: VPIN3.2, X1.6
unnamed: VPIN4.1, X1.7
unnamed: VPIN4.2, X1.8
unnamed: VPIN5.2, X1.10
unnamed: VPIN6.1, X1.11
unnamed: VPIN6.2, X1.12
unnamed: R3.P$2 (2), TN2TR.3 (E), TN2_555.4, TN2_555.8
unnamed: JP4.3, LCKAMP.3
unnamed: JP1.1, X1.4
unnamed: JP2.1, X1.13
unnamed: R8.P$2 (2), X1.16
unnamed: R9.P$2 (2), TN1TR.2 (C), TN2TR.2 (C), VREG_5V.OUT

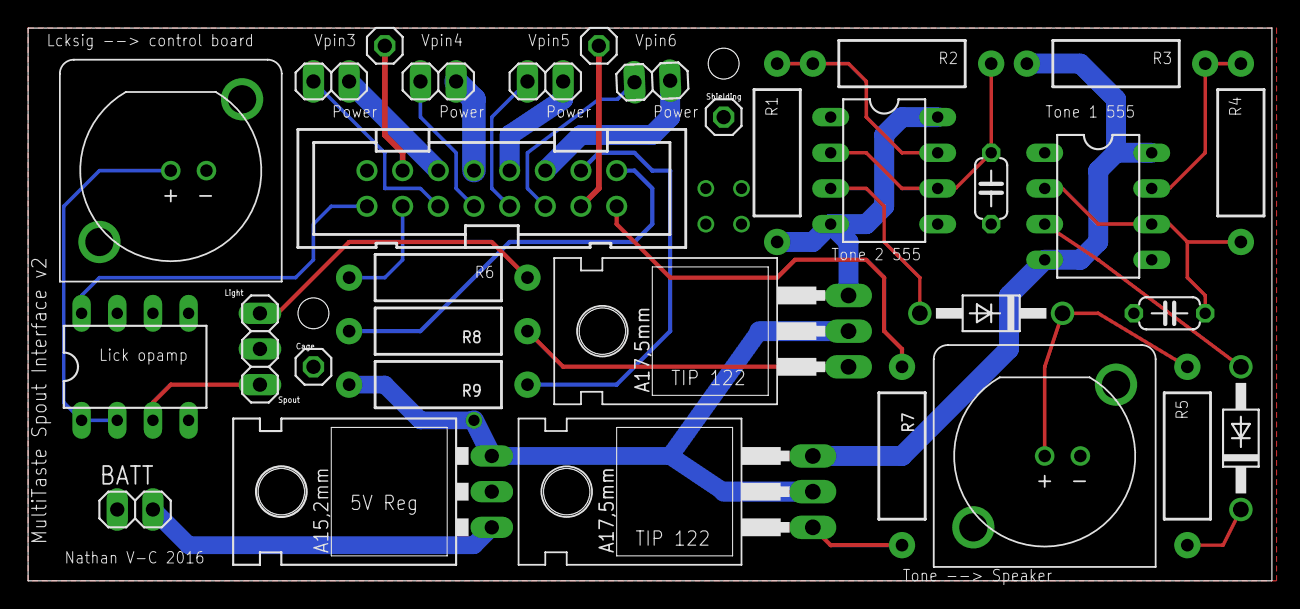
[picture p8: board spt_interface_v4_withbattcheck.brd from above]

Board: 2 copper layers, 88.6 x 39.4 mm, 32 parts (0 on the bottom side), 33 nets.

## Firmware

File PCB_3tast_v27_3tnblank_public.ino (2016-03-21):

 
// Arduino Script for MultiTastant Spout
// -----------
// When combined with the Multi Tastant Spout Arduino shield, spout interface board, and spout
// assembly, and an analog input signal to cue trial type, this script can run a repeated trial
// combined approach/avoidance learning task designed for rodents. Designed for Arduino Uno. 
// ----------
// See construction and experimental information at http://github/nathanvc/MultiTastantSpout
// Nathan V-C
// 7/2014-7/2015, 11/2015, 3/2016
// -----------

//----------------
// trial types indicated with analog input on trial_type_pin, 
// ---------------
// Active trials: 
// ---------------
// 2-3.5 seconds of water + light cue, followed by 400-1000ms tone, followed by 1.5-3 s tastant delivery,
// lick must be detected within 1000ms for full trial, otherwise light turns off and enters new timeout period
// Light remains on for full trial. 
// Water only "easy" keeps light on 3.9-7.5 seconds and delivers water, but does not require lick within 1000ms 
// Not all analog values are in an intuitive order, for historical task design reasons
//----------------
// Trial Type               Voltage in  Arduino units   Range of units read
//-----------               ----------  -------------   -------------------
// water easy & no tone,    0.25v       51.1.3          25-75
// water & no tone,         0.5v        102.3           76-153
// tone A & tast 1          1v          204.6           154-234
// Tone C & tast 1          1.25v       255.75          235-276
// tone B & tast 2          1.5v        306.9           277-358 
// tone B & tast 1          2v          409.2           359-439
// Tone C & tast 2          2.25v       460.35          440-480
// tone A & tast 2          2.5v        511.5           481-562
// tone A & water           3v          613.8           563-644
// Tone C & water           3.25v       664.95          645-685
// Tone B & water           3.5v        716.1           686-756
// --------
// Passive trials
// --------
// Tone presented and tastant delivered, without light cue or requirement to lick quickly
// Catch trials are no tone and no tastant, but occur with same time features as usual tone trials 
// used to detect false positive rate
//--------
// Trial Type                       Voltage in  Arduino units   Range of units read
//-----------                       ----------  -------------   -------------------
// Tone C, no light, tast 1,        3.8v        777.48          757-797
// Tone A only, no light, tast 1,   4 v         818.4           798-838
// Tone B only, no light, tast 2,   4.2v        859.32          839-879
// Tone B only, no light, tast 1,   4.4v        900.24          880-920
// Tone A only, no light, tast 2,   4.6v        941.16          921-961
// Tone C, no light, tast 2,        4.8v        982.08          962-1002
//----------------
// Costa Trial
// ---------------
// An alternate task on the same set up. 
// Long single trial, modeled after Costa et al., 2006 task, where tastant is delivered for a long (45 min) block
// Here altered with a light cue as opposed to a shutter, and fluid delivered every 10 licks,
// In contrast to delivery at a standard sipper tube, flued runs through a fourth mixed "vac" valve to avoic
// contamination of pure tastant lines
// ----------------
// Trial Type               Voltage in  Arduino units   Range of units read
//-----------               ----------  -------------   -------------------
// Costa trial              4.95V       1013            1003+
//-----------
//***********
// NOTE: that there are alternate "PORT" commands to write directly to the pins that can replace "digitalwrite", here they are commented out. 
// This option can speed things up faster than using digitalwrite but not on a time scale that mattered for this prep, 
// and you have to make sure you get your pin mappings correct if you use these (these map to the pins set in the header). 
// but if you use the PORT commands, you need to change in each command directly
//-----------

// INITIALIZE PINS
// ---------------
// electrical lick sensor pin
int elick_pin=A5;

// pin to sense battery power
int batt_check_pin=A1;

// analog signal that indicats which trial type to run when a mouse initiates a trial
int trial_type_pin=A0;    

// unused pin for reading to reduce digital noise on last read pin
int dummy_pin = A4;       

// pins to trigger opening valves for tastants
int water_out = 6; 
int tast_out_a = 5; // default is sugar
int tast_out_b = 4; // default is quinine
int vac_out = 3;  // this is an optional vac line, or a line for delivering tastants for the costa task
int light_out = 11;  // pin for cue light, needs to be the same as led_c_pin
int del_lick_pin = 13;  // indicates licks where fluid was delivered (for data acquisition)

// indicator LEDs
int led_a_pin = 9;  // indicates tastant a (sugar) is available
int led_b_pin = 10; // indicates tastant b (quinine) is available
int led_c_pin = 11; // needs to be same as light_out, indicates fluid available (and also high when light in cage is on)
int led_d_pin = 12; // indicates detected licks

// button pin input, used for loading and calibrating lines
// button is only detected when there is no active run
int button_pin=17;  //This is A3 -- Analog pin being used as digital input, 
                    //Digital analog can be a problem near analog in, but button should never be active when running a session

// pin to report difficulty (licks skipped before next tastant delivery)
// this pin also conveys specific timing information per trial (trial start, and length of learning period on active trials)
int countlick_pin = 8;
int speak_pin = 2; // tone A pin, tone plays if pin is high
int speak_pin_2 = 7; // tone B pin, tone plays if pin is high
                     // Tone C is both tones simultaneously


// --------
// INITIALIZE VARIABLES, THRESHOLDS AND COUNTERS
// --------
// threshold of voltage change to detect a lick, 
// if your rig is noisy, may need to change to be higher, or use pure threshold not difference threshold
int elick_diff_thresh = 40; 
float rewardsize = 25; // time valve open for each reward in ms, on my rig this give about a 1 microliter delivery

// vaccuum and rinse control timing, not currently used, but there are functions here that can be used to rinse if you need it
int vacdelay = 300;   //
int vacduration = 200; //in ms
int rinsedelay = 450;
int rinseduration= 50;

int interval = 50; // interval for the pulses that indicate skiplick number (so skiplick is rounding to multiple of 50ms)
int pulseState = LOW; // variable that will be used to set the skiplick pin

// initialize variables for light cue and tastants
boolean light_arm = 0;
boolean lastlight_arm = 0;
boolean water_arm = 0;
boolean tast_a_arm = 0;
boolean lasttast_a_arm = 0; 
boolean tast_b_arm = 0;
boolean lasttast_b_arm = 0; 
boolean tast_c_arm = 0;
boolean lasttast_c_arm=0;
boolean deliver = 0;
boolean lasttone_b_arm = 0; 
boolean lasttone_a_arm = 0; 

// timing and button initialization
unsigned long currentms=0;
unsigned long lastms=0;
unsigned long last_off=0;
unsigned long last_lick=0;
unsigned long ButtonTime=0;
unsigned long lastButtonTime=0;
unsigned long lastlastButtonTime=0;
unsigned long tone_cue_time=0;
unsigned long checktm=0;
unsigned long last_reward_ind=0;

// more initialization...
int buttonState = 0;         // current state of the button
int lastButtonState = 0;     // previous state of the button
int buttonPushCounter = 0;   // count of button presses
int button_off = 0;          // time button turned off
int lick_break_time = 50;    // forced break between reward delivery, caps lick detection at 20Hz, which is double speed mice actually lick
long last_elick = -1;        // time of last lick
long last_rwd_time = 0;      // time of last delivered lick
int skiplicks = random(10,31);  // initialize skiplicks between 10 & 30 licks
int lickcounter = skiplicks-1;  // counter for how many licks since prior, setting as skiplicks-1 assures delivery on first lick
int count_pulse = 0;        // indicator for turning on/off difficulty signal (for data collection of skiplick variable for that trial)
int lickcount_trial = 0;    // counts licks during a trial
long timeout_retrig = 0;    // variable for time that a timeout restarts (i.e. tracks licks during timeouts)
int tone_ind = 0;           // indicator for type of tone to play on trial (1, 2, 3)
int tast_ind = 0;           // indicator for tastant to deliver on a trial (1 = sugar, 2= quinine)
int light_ind = 0;          // indicator for whether light turns on in a trial

// initialization for trial arming and calibration button
int trial_type=0;
boolean calibrate=0;
boolean button_valve=0;
boolean tone_a_arm=0;
boolean tone_b_arm=0;
boolean water_ind=0;
boolean easy_ind=0;  // determines if turn on the rapid shutoff for water only trials -- only used for shaping
boolean openvalves=0;
boolean closevalves=0;
boolean tonecal=0;
boolean trial_arm=0;
boolean info_arm=0;
boolean lasttrial_arm=0;
unsigned long lastrep=0;

// Variables for trial and timeout lengths in ms
boolean timeout=1; // start in a timeout
boolean lastto=1; // timeout on last loop through
int timeout_length=random(3000,6001);  // length of initial timeout, 3-6s
long start_tone_ms=0;
long switch_ms=0;
long end_trial_ms=0;
long trial_start_ms=0;

// SETUP
void setup() {                

  // initialize the digital pins as inputs and outputs as needed
  pinMode(water_out, OUTPUT);
  pinMode(tast_out_a, OUTPUT);
  pinMode(tast_out_b, OUTPUT);
  pinMode(light_out, OUTPUT);
  pinMode(vac_out, OUTPUT);
  pinMode(led_a_pin, OUTPUT);
  pinMode(led_b_pin, OUTPUT);
  pinMode(led_c_pin, OUTPUT);
  pinMode(led_d_pin, OUTPUT);
  pinMode(countlick_pin, OUTPUT);
  pinMode(del_lick_pin, OUTPUT);
  pinMode(speak_pin, OUTPUT);
  pinMode(speak_pin_2, OUTPUT);
  pinMode(button_pin, INPUT);
  
  analogReference(DEFAULT);

  // read in a new random seed
  randomSeed(10000*analogRead(A4));

  Serial.begin(9600); 
  digitalWrite(countlick_pin, LOW); 

  // during setup, check if the battery that drives the tones has low volgage (if it does, frequency changes)
  // read the voltage coming out of the voltage regulator that drives tones
  long battval = analogRead(batt_check_pin);
  
 //if not very close to 5V, then blink all lights. 
 // If all lights blink when turning on rig, turn off, change battery, and restart 
  if (battval < 1000) {
      for (int i=0; i <= 30; i++){
      all_light_on();
      delay(800);
      all_light_off();
      delay(200);
      }
    }
  }
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

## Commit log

2016-05-03 Update PCBs, add IR option
    [3tastsp_v4_resistorcooldrive_battcheck.GBL, 3tastsp_v4_resistorcooldrive_battcheck.GBP, 3tastsp_v4_resistorcooldrive_battcheck.GTL, 3tastsp_v4_resistorcooldriv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]
2016-05-28 add parts list, update arduino with pin assignment for new PCBs
    [MultiTastantSpout_partslist.xlsx]

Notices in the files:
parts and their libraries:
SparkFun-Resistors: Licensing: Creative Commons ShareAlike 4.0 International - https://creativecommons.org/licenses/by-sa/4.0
